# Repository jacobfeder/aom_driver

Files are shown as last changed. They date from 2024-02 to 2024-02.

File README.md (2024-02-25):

# 2-Tone AOM driver
This custom acousto-optic modulator (AOM) driver PCB is designed for generating short light pulses with enhanced isolation and power stability compared to traditional AOM configurations.

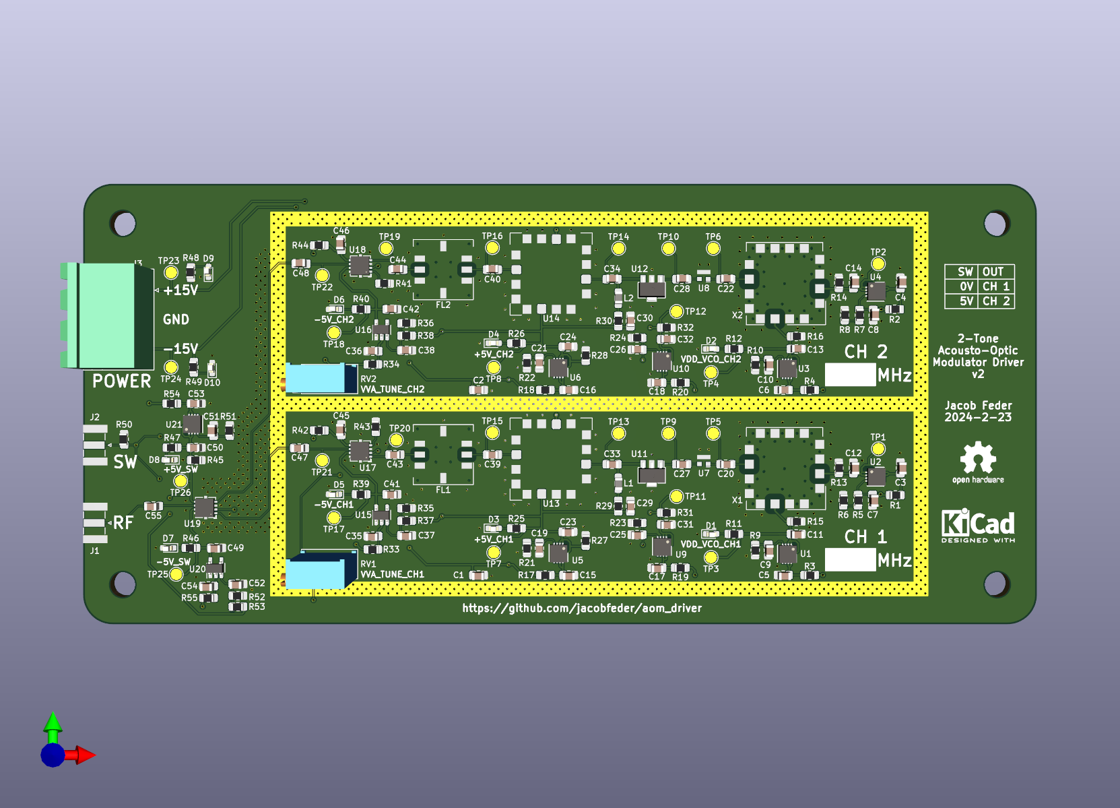
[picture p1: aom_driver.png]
AOM PCB rendering


# Background
When generating light pulses with an AOM, two parameters that you may care about are the isolation and power stability.

The isolation (usually expressed in dB) is defined as $10*\log_{10}(P_{on} / P_{off})$, where $P_{on}$ is the transmitted optical power with the AOM enabled, and $P_{off}$ is the transmitted optical power with the AOM disabled. A low isolation means that even when the AOM is disabled, there is significant light leakage through the AOM, which can be undesirable for certain applications.

Power stability is the change in transmitted optical power as a function of time or AOM duty cycle. The active area of an AOM that the optical beam passes through is made of a material whose optical index of refraction changes with strain (acoustic waves), producing the desired beam diffraction. However, other variables, such as temperature, can impact the index of refraction and, therefore, the pointing stability of the beam.

Many traditional AOM drivers are used as follows:
- The driver produces a single frequency which is toggled on and off, often with relatively low isolation.
- The optical power is switched between being primarily concentrated in the 0th order diffraction peak (AOM disabled, RF off) and the 1st order peak (AOM enabled, RF on).

This configuration produces two undesirable effects. First, drivers with low isolation (RF power $P_{on}/P_{off}$) can limit the optical isolation of the AOM due to parasitic driving of the AOM with RF leakage. Second, when switching the RF drive on/off, there is a change in RF power dissipation in the AOM crystal, inducing a temperature change. This temperature change reduces the beam pointing stability and produces power fluctuations as a function of time and switching duty cycle.

# Overview

The 2-Tone AOM driver greatly mitigates isolation and power stability issues. Whereas traditional AOM drivers rapidly switch between an RF signal being on or off, this driver rapidly switches between two different RF frequencies. The optical power diffracted by the AOM with low-frequency drive should ideally be fiber coupled into a single-mode fiber and then used in your down-stream application. The optical power diffracted by the AOM with the high-frequency "dummy" drive should be sent into a beam-dump. If the power of the two frequencies produced by this driver are properly calibrated, thermalization effects of the AOM crystal can be minimized because the RF power delivered to the crystal is equal for both frequencies. The driver can switch between these two frequencies with very high RF isolation such that the achievable AOM optical isolation will likely become limited by the physics of gaussian optics (see additional notes below).

# Specifications
- RF isolation ~90dB
- Both frequency outputs individually tunable from ~0dBm to <-30dBm (before amplifier, >30dBm after amplifier)
- Frequency range accessible with default VCO 140 - 250 MHz (much larger range possible by swapping VCO, see customization section)
- At the time of writing, cost is <$1000 for all parts
- Convenient DIN rail mounting
- TTL input switches between the two frequencies

# Principle of Operation
The driver consists of four main parts: two nearly-identical frequency synthesis sections, a fast RF switch to select the frequency, and an (off board) RF amplifier. The frequency synthesis sections begin with a voltage-controlled oscillator (VCO) that generates the initial RF signal (CVCO55xx). A fixed attenuator limits the maximum output power (PAT1220-C-x). Next, an amplifier increases the output power (GVA-81). A voltage-variable attenuator (VVA) allows the user to tune the output power of each frequency synthesis channel in real-time using a potentiometer in order to calibrate the system (RVA-3000R). A filter reduces some of the harmonics (RLP-xxx+). An RF switch (M3SWA-2-50DRB+) for each frequency synthesis channel toggles the frequency on/off before the final switch in order to increase isolation. This concludes the frequency synthesis sections. A final RF switch (M3SWA-2-50DRB+) selects the output frequency channel. The AOM driver output is intended to then be fed to an external RF amplifier.

# Required Parts
- The 2-tone AOM driver PCB (see aom_driver.csv for PCB BOM)
- +-15V DC power supply for the AOM driver PCB, recommend TODO
- RF amplifier, recommend [Minicircuits ZHL-03-5WF+](https://www.minicircuits.com/WebStore/dashboard.html?model=ZHL-03-5WF%2B)
- 24V DC power supply for the RF amplifier, recommend TODO

# Calibration
The goal of calibration is to adjust the output power of the two driver frequency channels such that they deliver the same RF power to the AOM crystal, minimizing power fluctuations due to thermalization. A good starting point is to measure the $S_{11}$ of the AOM itself using a network analyzer, and pick your two RF frequencies to have a similar $S_{11}$. Keeping the frequencies as far apart as possible may be important to maximize optical isolation (see additional notes section). Once the frequencies are selected, set up the whole system to drive the AOM. First, the primary frequency that will be used in your downstream application should be adjusted using the potentiometer to get the desired output RF power for the desired AOM diffraction efficiency. Keep in mind that using higher power will generally tend to exacerbate thermalization issues. Next, disconnect the driver PCB from the RF power amp and measure the output power of the driver PCB. Adjust the second "dummy" frequency to have similar power to the primary frequency. At this point, the two frequencies should be delivering pretty similar heat loads to the AOM. Final tuning can be performed by observing the pulse characteristics using a photodiode (with sufficient bandwidth). Connect the photodiode to an oscilloscope and toggle the AOM with very long period (e.g. 1 minute). You should be able to observe a fast rise (ns-scale, due to the AOM acoustic wave propagation), followed by a very slow drift (seconds-scale, due to thermalization). Now, finely adjust the dummy frequency until the the slow drift is minimized.

# Customization
The driver is designed to be easily customized. The critical components were chosen such that they can be swapped out with pin-pin compatible components with different characteristics.

### Frequency
The VCO can be substituted for nearly any member of the [Crystek CVCO55 series](https://www.crystek.com/home/vco/cvco55.aspx), which should accomodate a widge range of AOM drive frequencies. By default, the schematic is configured to output 150 MHz and 250 MHz. The VCO specified in the schematic has a range of 140 - 250 MHz. Changing the frequency in this range can be accomplished by configuring resistors $R_{5}$, $R_{6}$ for channel 1 and $R_{7}$, $R_{8}$ for channel 2. The VCO output frequency as a function of tuning voltage is given by the tuning curve in the [datasheet](https://www.crystek.com/specification/vco/CVCO55CW-0140-0250.pdf). The VCO tuning voltage is $10 \text{uA} * (R_5 + R_6)$ for channel 1, and $10 \text{uA} * (R_7 + R_8)$ for channel 2. For example, let's imagine you wanted an output frequency of 200 MHz on channel 1. The CVCO55CW-0140-0250 tuning curve shows that you would need a tuning voltage of 6 V. Then you would set $R_5 + R_6 = 6 \text{V} / 10 \text{uA} = 600 \text{kOhm}$. Similarly, resistors $R_{9}$ and $R_{10}$ set the VCO power supply voltages and can be substituted as needed according to $V_{CC1} = 10 \text{uA} * R_{9}$ and $V_{CC2} = 10 \text{uA} * R_{10}$. When changing the drive frequency, filters FL1 and FL2 should potentially be changed in order to accomodate the new frequency. They should be chosen such that the primary frequency is minimally attenuated, but harmonics are maximally attenuated. However, attenuating harmonics may not have a significant impact on the performance for reasons explained in the additional notes section.

### Power
The final RF output power of the system is impossible to predict precisely due to the tolerance stackup of all the components, which is why the board contains a potentiometer for individually tuning the output power of each frequency synthesis channel as well as a power-limiting fixed attenuator. The driver PCB should be capable of outputting a maximum power of >0dBm. The [Minicircuits ZHL-03-5WF+](https://www.minicircuits.com/WebStore/dashboard.html?model=ZHL-03-5WF%2B) has a gain of >30dB, so the final output power that can be achieved before the AOM is in excess of 1W. AOMs (and power amplifiers) can be damaged by too much input power. For this reason, a fixed attenuator PAT1220-C-x is included (U7 and U8) to limit the driver PCB maximum output power. Before connecting the driver PCB to the RF amplifier or AOM, the driver PCB output power should be measured. It is recommended to pick a specific PAT1220-C-x fixed attenuator for U7 and U8 in order to limit the maximum output power for your given RF amplifier and AOM such that no damage to either component is possible when the VVA poteniometer is tuned to output the maximum power from the driver PCB.

# Additional Notes
- The AOM driver system will cause the AOM to produce several optical beams at its output due to both AOM physics and RF design. When the low-frequency RF path is selected, it will produce 0th, 1st, 2nd, ..., nth order beams. The 1st order beam is the desired optical output and should go to the downstream application. All other 0th, 2nd, etc. order beams should be blocked or otherwise not coupled into the optical output. When the high frequency is selected, it will also produce 0th, 1st, 2nd, ..., nth order beams. All of these beams are "dummy" beams and should be blocked or otherwise not coupled into the downstream application. It is important to use the 1st order low-frequency beam for your application, as it will have minimal interference from RF drive harmonics.
- While the AOM driver has very high RF isolation, achieving high optical isolation requires additional careful attention to detail with optical design. I would recommend fiber coupling the 1st order low-frequency beam after the AOM for best performance.
- If all beams except the low-frequency 1st order beam are sufficiently blocked, the optical isolation will likely become limited by gaussian optics considerations. A beam of light entering the AOM will always have some finite divergence. After exiting the AOM, many beams are generated as explained above. These undesired beams will always have some degree of coupling into the desired output path due to their finite divergence, limiting the total optical isolation. A script is provided (TODO) to help with calculating the optical isolation. There is a somewhat intuitive explanation for this optics-limited isolation by consdering the tradeoff between isolation, rise-time, and AOM RF bandwidth. Getting a faster rise-time requires a smaller optical spot size on the AOM crystal, which requires a higher beam divergence. Higher divergence results in reduced isolation as explained above. Higher AOM RF bandwidth allows the primary and "dummy" beams to be separated by a larger angle, which increases their isolation. Therefore, it is important to consider the RF bandwidth when selecting an AOM, and the desired isolation and rise-time when selecting lenses to focus the beam onto the AOM crystal.

Feel free to email me if you have any questions at <jacobsfeder@gmail.com>.

# Acknowledgements
- This project would not have been possible without the help of Arron Campi at Gooch and Housego. He graciously provided his time and insight by helping me to understand AOM physics and limitations, as well as suggesting the idea of driving the AOM with multiple frequencies.
- Ben Soloway contributed the script that calculates optical isolation, and provided comic relief in addition to being my scientific partner in crime.
- The Awschalom Lab at UChicago and the NSF provided financial support.

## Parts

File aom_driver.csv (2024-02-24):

Source: | /home/jf/projects/aom_driver/aom_driver.kicad_sch
Date: | Sat 24 Feb 2024 12:10:03 PM CST
Tool: | Eeschema 7.0.10-7.0.10~ubuntu22.04.1
Generator: | /usr/share/kicad/plugins/bom_csv_grouped_by_value.py
Component Count: | 158
Collated Components:
Item | Qty | Reference(s) | Value | LibPart | Footprint | Datasheet | DNP | DKPN | MF | MFPN | Sim.Enable
1 | 43 | C1, C2, C3, C4, C5, C6, C11, C12, C13, C14, C15, C16, C17, C18, C20, C22, C23, C24, C27, C28, C29, C30, C31, C32, C33, C34, C35, C36, C39, C40, C41, C42, C43, C44, C45, C46, C47, C48, C49, C50, C53, C54, C55 | 2.2u | Device:C | Capacitor_SMD:C_0805_2012Metric_Pad1.18x1.45mm_HandSolder | ~ |  | 1276-2953-1-ND | Samsung Electro-Mechanics | CL21B225KAFNFNE
2 | 9 | C7, C8, C9, C10, C19, C21, C25, C26, C51 | 0.1u | Device:C | Capacitor_SMD:C_0805_2012Metric_Pad1.18x1.45mm_HandSolder | ~ |  | 1276-1099-1-ND | Samsung Electro-Mechanics | CL21B104KACNNNC
3 | 3 | C37, C38, C52 | 0.1u | Device:C | Capacitor_SMD:C_0805_2012Metric_Pad1.18x1.45mm_HandSolder | ~ | DNP | 1276-1099-1-ND | Samsung Electro-Mechanics | CL21B104KACNNNC
4 | 10 | D1, D2, D3, D4, D5, D6, D7, D8, D9, D10 | LED | Device:LED | LED_SMD:LED_0603_1608Metric_Pad1.05x0.95mm_HandSolder | ~ |  | 475-LTQ39G-Q1OO-25-1CT-ND | ams-OSRAM USA INC. | LT Q39G-Q1OO-25-1
5 | 1 | DRA1 | DIN_Rail_Adapter | Mechanical:DIN_Rail_Adapter |  | ~ |  |  | Winford Engineering | DINM30
6 | 1 | FL1 | RLP-320+ | RF_Filter:RLP-158 | RF_Mini-Circuits:Mini-Circuits_GP731_LandPatternPL-176 | https://www.minicircuits.com/pdfs/RLP-320+.pdf |  | 3157-RLP-320+CT-ND | Mini-Circuits | RLP-320+
7 | 1 | FL2 | RLP-158 | RF_Filter:RLP-158 | RF_Mini-Circuits:Mini-Circuits_GP731_LandPatternPL-176 | https://www.minicircuits.com/pdfs/RLP-158+.pdf |  | 3157-RLP-158+CT-ND | Mini-Circuits | RLP-158+
8 | 4 | H1, H2, H3, H4 | MountingHole | Mechanical:MountingHole | MountingHole:MountingHole_4.3mm_M4_DIN965 | ~ |  |  | McMaster-Carr | 91292A108
9 | 2 | J1, J2 | Conn_Coaxial | Connector:Conn_Coaxial | Connector_Coaxial:SMA_Samtec_SMA-J-P-X-ST-EM1_EdgeMount | ~ |  | 2057-RF2-143-T-17-50-G-ND | Adam Tech | RF2-143-T-17-50-G
10 | 1 | J3 | Screw_Terminal_01x03 | Connector:Screw_Terminal_01x03 | Connector_Phoenix_MSTB:PhoenixContact_MSTBA_2,5_3-G-5,08_1x03_P5.08mm_Horizontal | ~ |  | 277-1107-ND | Phoenix Contact | 1757255
11 | 1 | J4 | Screw_Terminal_01x03 | Connector:Screw_Terminal_01x03 |  | ~ |  | 277-1012-ND | Phoenix Contact | 1757022
12 | 2 | L1, L2 | 10u | Device:L | Inductor_SMD:L_0805_2012Metric_Pad1.05x1.20mm_HandSolder | ~ |  | 445-8656-1-ND | TDK Corporation | MLZ2012M100HT000
13 | 17 | R1, R2, R3, R4, R8, R17, R18, R19, R20, R29, R30, R33, R34, R42, R44, R54, R55 | 0 | Device:R | Resistor_SMD:R_0805_2012Metric_Pad1.20x1.40mm_HandSolder | ~ |  | 311-0.0ARCT-ND | YAGEO | RC0805JR-070RL
14 | 1 | R5 | 10M | Device:R | Resistor_SMD:R_0805_2012Metric_Pad1.20x1.40mm_HandSolder | ~ |  | 311-10.0MCRCT-ND | YAGEO | RC0805FR-0710ML
15 | 1 | R6 | 49.9k | Device:R | Resistor_SMD:R_0805_2012Metric_Pad1.20x1.40mm_HandSolder | ~ |  | 311-49.9KCRCT-ND | YAGEO | RC0805FR-0749K9L
16 | 1 | R7 | 150k | Device:R | Resistor_SMD:R_0805_2012Metric_Pad1.20x1.40mm_HandSolder | ~ |  | 311-150KCRCT-ND | YAGEO | RC0805FR-07150KL
17 | 11 | R9, R10, R21, R22, R35, R36, R37, R38, R51, R52, R53 | 499k | Device:R | Resistor_SMD:R_0805_2012Metric_Pad1.20x1.40mm_HandSolder | ~ |  | 311-499KCRCT-ND | YAGEO | RC0805FR-07499KL
18 | 8 | R11, R12, R25, R26, R39, R40, R46, R47 | 4.7k | Device:R | Resistor_SMD:R_0805_2012Metric_Pad1.20x1.40mm_HandSolder | ~ |  | 13-RC0805FR-134K7LCT-ND | YAGEO | RC0805FR-134K7L
19 | 9 | R13, R14, R15, R16, R27, R28, R31, R32, R45 | 1.5k | Device:R | Resistor_SMD:R_0805_2012Metric_Pad1.20x1.40mm_HandSolder | ~ |  | 311-1.50KCRCT-ND | YAGEO | RC0805FR-071K5L
20 | 2 | R23, R24 | 2.7M | Device:R | Resistor_SMD:R_0805_2012Metric_Pad1.20x1.40mm_HandSolder | ~ |  | 13-RC0805FR-072M7LCT-ND | YAGEO | RC0805FR-072M7L
21 | 3 | R41, R43, R50 | 49.9 | Device:R | Resistor_SMD:R_0805_2012Metric_Pad1.20x1.40mm_HandSolder | ~ |  | 311-49.9CRCT-ND | YAGEO | RC0805FR-0749R9L
22 | 2 | R48, R49 | 27k | Device:R | Resistor_SMD:R_0805_2012Metric_Pad1.20x1.40mm_HandSolder | ~ |  | 311-27.0KCRCT-ND | YAGEO | RC0805FR-0727KL
23 | 2 | RV1, RV2 | 2M | Device:R_Potentiometer | Potentiometer_THT:Potentiometer_Bourns_3296X_Horizontal | ~ |  | 3296X-205LF-ND | Bourns Inc. | 3296X-1-205LF
24 | 9 | U1, U2, U3, U4, U5, U6, U9, U10, U21 | LT3082xDD | Regulator_Linear:LT3082xDD | Package_DFN_QFN:DFN-8-1EP_3x3mm_P0.5mm_EP1.66x2.38mm | https://www.analog.com/media/en/technical-documentation/data-sheets/3082f.pdf |  | LT3082EDD#TRPBFCT-ND | Analog Devices Inc. | LT3082EDD#TRPBF
25 | 2 | U7, U8 | PAT1220-C-8DB | RF:PAT1220-C-8DB | RF_Converter:RF_Attenuator_Susumu_PAT1220 | https://www.susumu.co.jp/common/pdf/n_catalog_partition16_en.pdf |  | PAT120CT-ND | Susumu | PAT1220-C-0DB-T5
26 | 2 | U11, U12 | GVA-81 | RF_Amplifier:GVA-81 | Package_TO_SOT_SMD:SOT-89-3 | https://www.minicircuits.com/pdfs/GVA-81+.pdf |  | 3157-GVA-81+CT-ND | Mini-Circuits | GVA-81+
27 | 2 | U13, U14 | RVA-3000R | RF:RVA-3000R | RF_Mini-Circuits:Mini-Circuits_DV874_LandPatternPL-040 | https://www.minicircuits.com/pdfs/RVA-3000R+.pdf |  | 3157-RVA-3000R+CT-ND | Mini-Circuits | RVA-3000R+
28 | 3 | U15, U16, U20 | ADP7182AUJZ-5.0 | Regulator_Linear:ADP7182AUJZ-5.0 | Package_TO_SOT_SMD:TSOT-23-5 | https://www.analog.com/media/en/technical-documentation/data-sheets/ADP7182.pdf |  | 505-ADP7182AUJZ-5.0-R7CT-ND | Analog Devices Inc. | ADP7182AUJZ-5.0-R7
29 | 3 | U17, U18, U19 | M3SWA-2-50 | RF_Switch:M3SWA-2-50 | Package_DFN_QFN:Mini-Circuits_DL805 | https://www.minicircuits.com/pdfs/M3SWA-2-50DRB+.pdf |  | 3157-M3SWA-2-50DRB+CT-ND | Mini-Circuits | M3SWA-2-50DRB+
30 | 2 | X1, X2 | CVCO55xx | Oscillator:CVCO55xx | RF_Mini-Circuits:Mini-Circuits_CK605_LandPatternPL-012 | https://www.crystek.com/home/vco/cvco55.aspx |  | 744-1204-ND | Crystek Corporation | CVCO55CW-0140-0250

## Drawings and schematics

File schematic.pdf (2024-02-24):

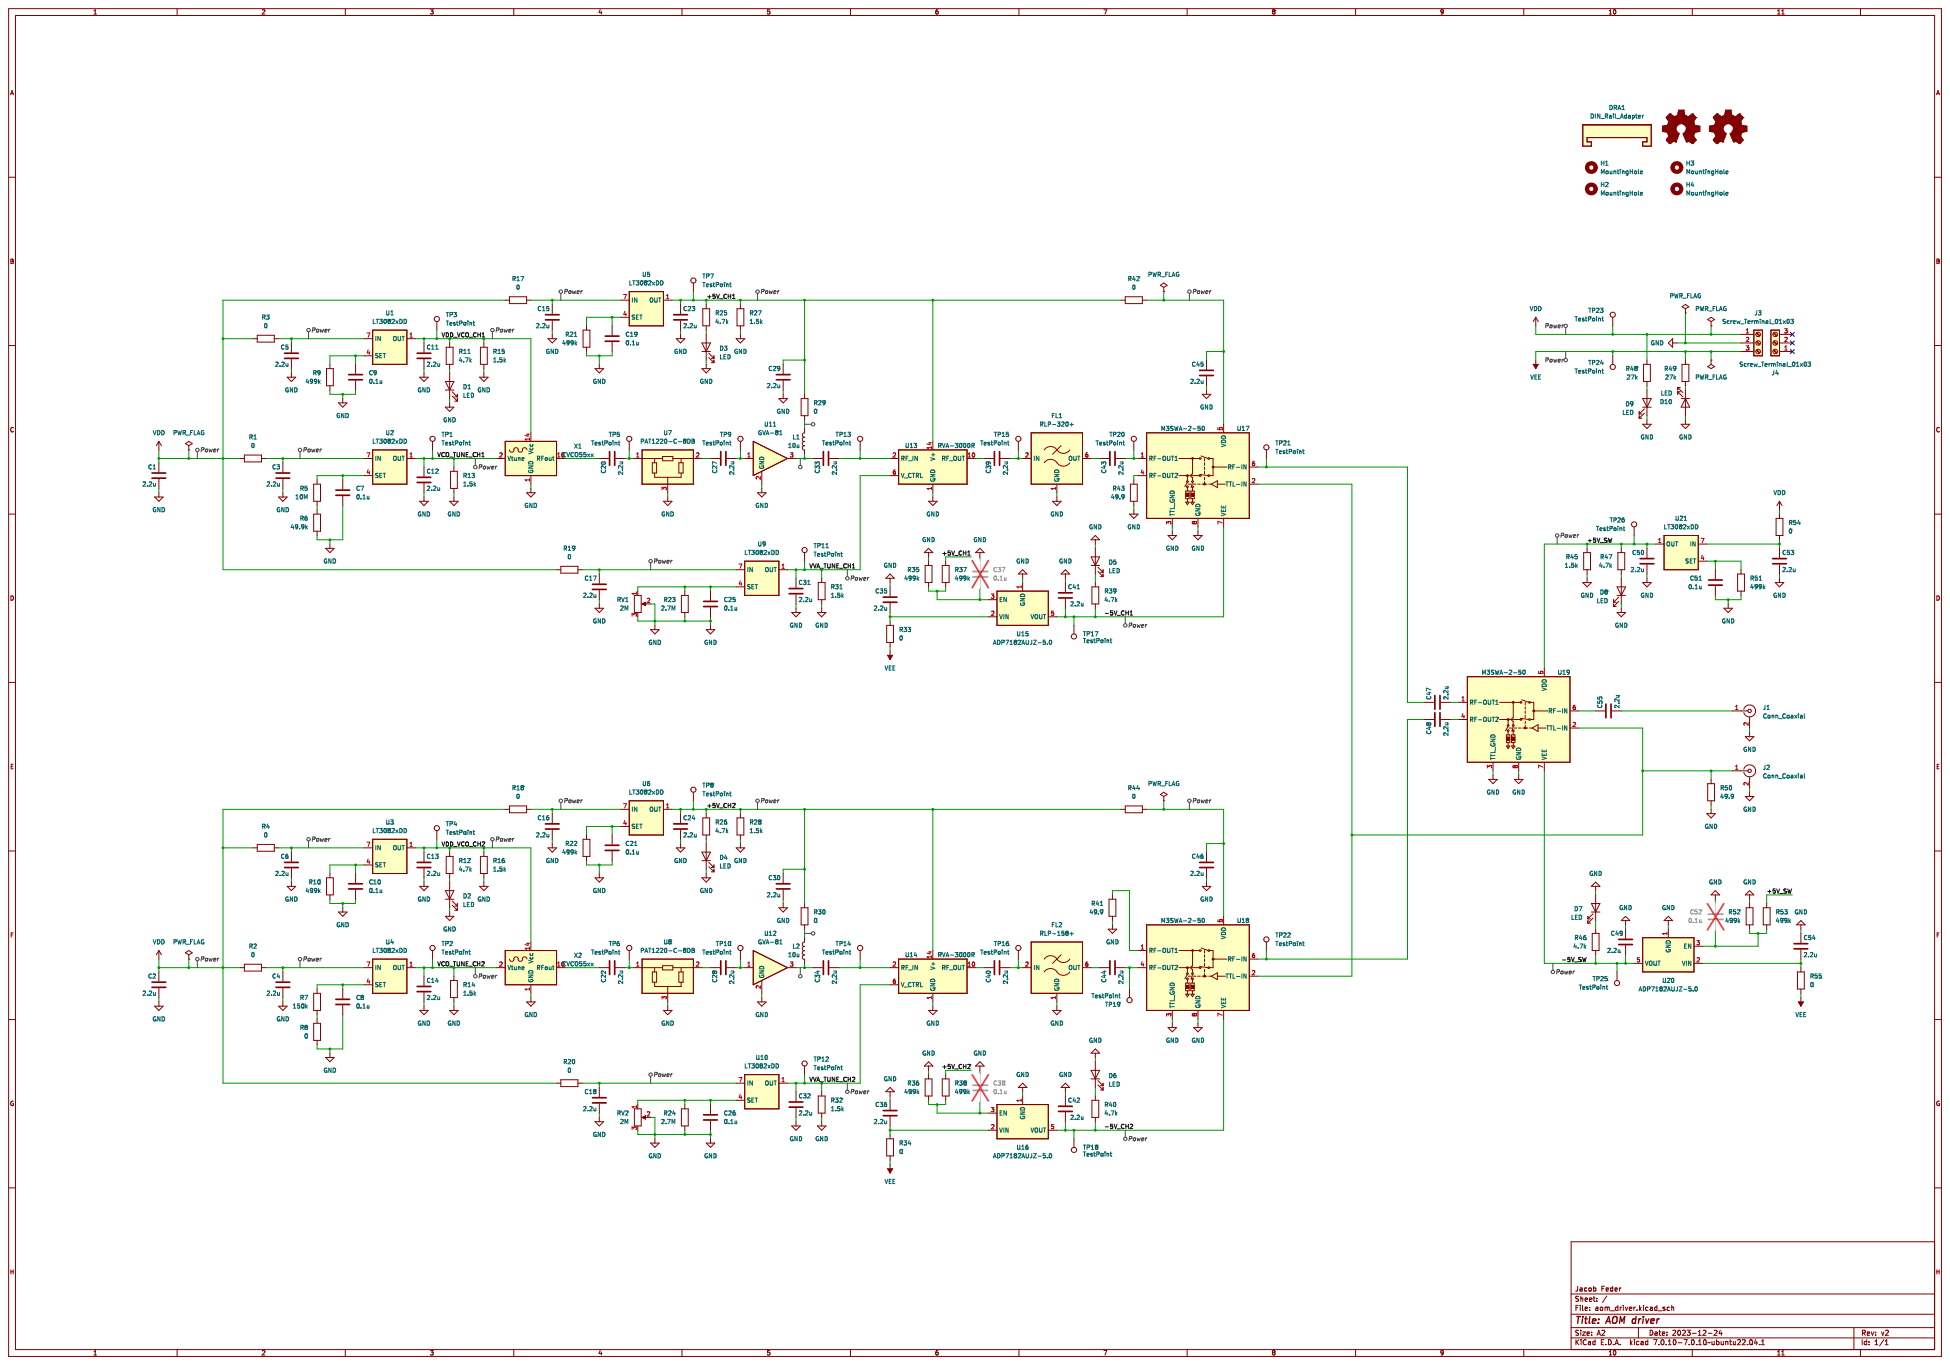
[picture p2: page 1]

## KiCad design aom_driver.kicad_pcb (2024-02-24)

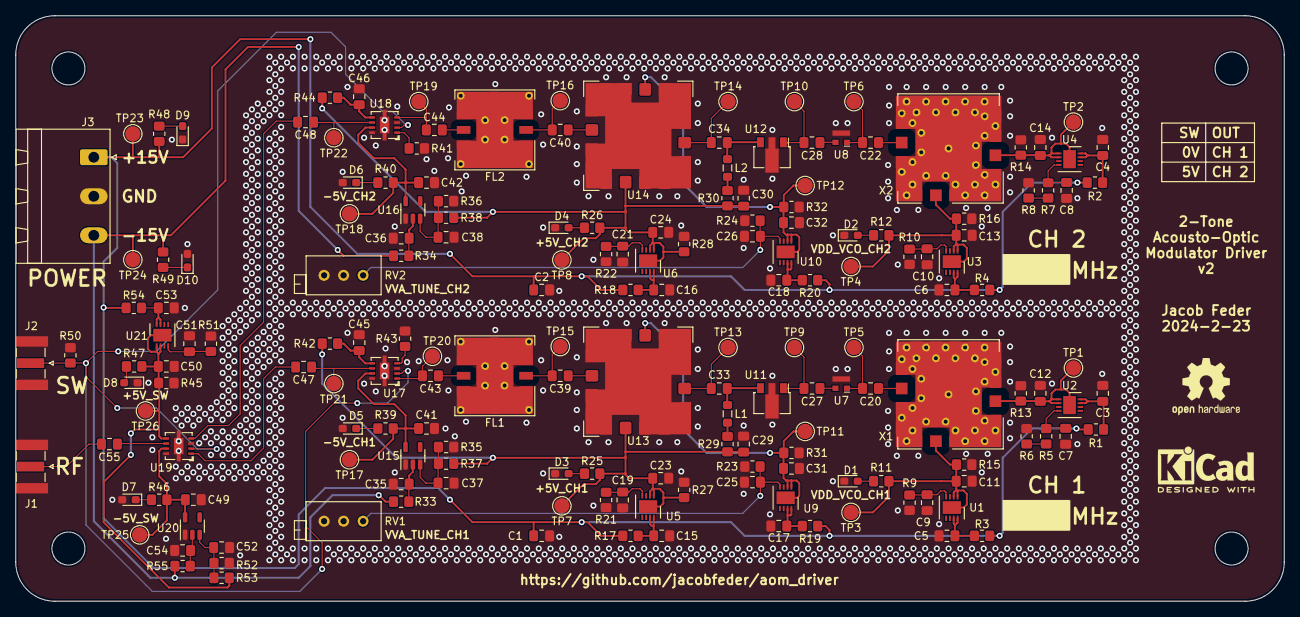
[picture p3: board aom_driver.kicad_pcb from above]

Board: 4 copper layers, 165.1 x 76.2 mm, 184 parts (0 on the bottom side), 84 nets.

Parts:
C1, C2, C3, C4, C5, C6, C11, C12, C13, C14, C15, C16, C17, C18, C20, C22, C23, C24, C27, C28, C29, C30, C31, C32, C33, C34, C35, C36, C39, C40, C41, C42, C43, C44, C45, C46, C47, C48, C49, C50, C53, C54, C55: 2.2u; C_0805_2012Metric_Pad1.18x1.45mm_HandSolder
C7, C8, C9, C10, C19, C21, C25, C26, C37, C38, C51, C52: 0.1u; C_0805_2012Metric_Pad1.18x1.45mm_HandSolder
D1, D2, D3, D4, D5, D6, D7, D8, D9, D10: LED; LED_0603_1608Metric_Pad1.05x0.95mm_HandSolder
FL1: RLP-320+; Mini-Circuits_GP731_LandPatternPL-176
FL2: RLP-158; Mini-Circuits_GP731_LandPatternPL-176
H1, H2, H3, H4: MountingHole; MountingHole_4.3mm_M4_DIN965
J1, J2: Conn_Coaxial; SMA_Samtec_SMA-J-P-X-ST-EM1_EdgeMount
J3: Screw_Terminal_01x03; PhoenixContact_MSTBA_2,5_3-G-5,08_1x03_P5.08mm_Horizontal
L1, L2: 10u; L_0805_2012Metric_Pad1.05x1.20mm_HandSolder
R1, R2, R3, R4, R8, R17, R18, R19, R20, R29, R30, R33, R34, R42, R44, R54, R55: 0; R_0805_2012Metric_Pad1.20x1.40mm_HandSolder
R5: 10M; R_0805_2012Metric_Pad1.20x1.40mm_HandSolder
R6: 49.9k; R_0805_2012Metric_Pad1.20x1.40mm_HandSolder
R7: 150k; R_0805_2012Metric_Pad1.20x1.40mm_HandSolder
R9, R10, R21, R22, R35, R36, R37, R38, R51, R52, R53: 499k; R_0805_2012Metric_Pad1.20x1.40mm_HandSolder
R11, R12, R25, R26, R39, R40, R46, R47: 4.7k; R_0805_2012Metric_Pad1.20x1.40mm_HandSolder
R13, R14, R15, R16, R27, R28, R31, R32, R45: 1.5k; R_0805_2012Metric_Pad1.20x1.40mm_HandSolder
R23, R24: 2.7M; R_0805_2012Metric_Pad1.20x1.40mm_HandSolder
R41, R43, R50: 49.9; R_0805_2012Metric_Pad1.20x1.40mm_HandSolder
R48, R49: 27k; R_0805_2012Metric_Pad1.20x1.40mm_HandSolder
RV1, RV2: 2M; Potentiometer_Bourns_3296X_Horizontal
SYM1: Logo_Open_Hardware_Small; OSHW-Logo2_9.8x8mm_SilkScreen
SYM2: Logo_Open_Hardware_Small; KiCad-Logo2_5mm_SilkScreen
TP1, TP2, TP3, TP4, TP5, TP6, TP7, TP8, TP9, TP10, TP11, TP12, TP13, TP14, TP15, TP16, TP17, TP18, TP19, TP20, TP21, TP22, TP23, TP24, TP25, TP26: TestPoint; TestPoint_Pad_D2.0mm
U1, U2, U3, U4, U5, U6, U9, U10, U21: LT3082xDD; DFN-8-1EP_3x3mm_P0.5mm_EP1.66x2.38mm
U7, U8: PAT1220-C-8DB; RF_Attenuator_Susumu_PAT1220
U11, U12: GVA-81; SOT-89-3
U13, U14: RVA-3000R; Mini-Circuits_DV874_LandPatternPL-040
U15, U16, U20: ADP7182AUJZ-5.0; TSOT-23-5
U17, U18, U19: M3SWA-2-50; Mini-Circuits_DL805
X1, X2: CVCO55xx; Mini-Circuits_CK605_LandPatternPL-012

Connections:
/+5V_CH1: C23.1, C29.1, R25.1, R27.1, R29.1, R37.1, R42.1, TP7.1, U5.1 (OUT), U5.2 (OUT), U5.9 (OUT), U13.14 (V+)
/+5V_CH2: C24.1, C30.1, R26.1, R28.1, R30.1, R38.1, R44.1, TP8.1, U6.1 (OUT), U6.2 (OUT), U6.9 (OUT), U14.14 (V+)
/+5V_SW: C50.1, R45.1, R47.1, R53.1, TP26.1, U19.5 (VDD), U21.1 (OUT), U21.2 (OUT), U21.9 (OUT)
/-5V_CH1: C41.2, R39.2, TP17.1, U15.5 (VOUT), U17.7 (VEE)
/-5V_CH2: C42.2, R40.2, TP18.1, U16.5 (VOUT), U18.7 (VEE)
/-5V_SW: C49.2, R46.2, TP25.1, U19.7 (VEE), U20.5 (VOUT)
/VCO_TUNE_CH1: C12.1, R13.1, TP1.1, U2.1 (OUT), U2.2 (OUT), U2.9 (OUT), X1.2 (Vtune)
/VCO_TUNE_CH2: C14.1, R14.1, TP2.1, U4.1 (OUT), U4.2 (OUT), U4.9 (OUT), X2.2 (Vtune)
/VDD_VCO_CH1: C11.1, R11.1, R15.1, TP3.1, U1.1 (OUT), U1.2 (OUT), U1.9 (OUT), X1.14 (Vcc)
/VDD_VCO_CH2: C13.1, R12.1, R16.1, TP4.1, U3.1 (OUT), U3.2 (OUT), U3.9 (OUT), X2.14 (Vcc)
/VVA_TUNE_CH1: C31.1, R31.1, TP11.1, U9.1 (OUT), U9.2 (OUT), U9.9 (OUT), U13.6 (V_CTRL)
/VVA_TUNE_CH2: C32.1, R32.1, TP12.1, U10.1 (OUT), U10.2 (OUT), U10.9 (OUT), U14.6 (V_CTRL)
GND: C1.2, C2.2, C3.2, C4.2, C5.2, C6.2, C7.2, C8.2, C9.2, C10.2, C11.2, C12.2, C13.2, C14.2, C15.2, C16.2, C17.2, C18.2, C19.2, C21.2, C23.2, C24.2, C25.2, C26.2, C29.2, C30.2, C31.2, C32.2, C35.1, C36.1, C37.1, C38.1, C41.1, C42.1, C45.2, C46.2, C49.1, C50.2, C51.2, C52.1, C53.2, C54.1, D1.1 (K), D2.1 (K), D3.1 (K), D4.1 (K), D5.2 (A), D6.2 (A), D7.2 (A), D8.1 (K), D9.1 (K), D10.2 (A), FL1.1 (GND), FL1.3 (GND), FL1.4 (GND), FL1.5 (GND), FL1.7 (GND), FL1.8 (GND), FL2.1 (GND), FL2.3 (GND), FL2.4 (GND), FL2.5 (GND), FL2.7 (GND), FL2.8 (GND), J1.2 (Ext), J2.2 (Ext), J3.2, R6.1, R8.2, R9.2, R10.2, R13.2, R14.2, R15.2, R16.2, R21.2, R22.2, R23.2, R24.2, R27.2, R28.2, R31.2, R32.2, R35.1, R36.1, R41.2, R43.2, R45.2, R50.2, R51.2, R52.1, RV1.2, RV1.3, RV2.2, RV2.3, U7.3, U8.3, U11.2 (GND), U12.2 (GND), U13.1 (GND), U13.3 (GND), U13.4 (GND), U13.5 (GND), U13.7 (GND), U13.8 (GND), U13.9 (GND), U13.11 (GND), U13.12 (GND), U13.13 (GND), U13.15 (GND), U13.16 (GND), U14.1 (GND), U14.3 (GND), U14.4 (GND), U14.5 (GND), U14.7 (GND), U14.8 (GND), U14.9 (GND), U14.11 (GND), U14.12 (GND), U14.13 (GND), U14.15 (GND), U14.16 (GND), U15.1 (GND), U16.1 (GND), U17.3 (TTL_GND), U17.8 (GND), U17.9 (GND), U18.3 (TTL_GND), U18.8 (GND), U18.9 (GND), U19.3 (TTL_GND), U19.8 (GND), U19.9 (GND), U20.1 (GND), X1.1 (GND), X1.3 (GND), X1.4 (GND), X1.5 (GND), X1.6 (GND), X1.7 (GND), X1.8 (GND), X1.9 (GND), X1.11 (GND), X1.12 (GND), X1.13 (GND), X1.15 (GND), X1.16 (GND), X2.1 (GND), X2.3 (GND), X2.4 (GND), X2.5 (GND), X2.6 (GND), X2.7 (GND), X2.8 (GND), X2.9 (GND), X2.11 (GND), X2.12 (GND), X2.13 (GND), X2.15 (GND), X2.16 (GND)
unnamed: C3.1, R1.2, U2.7 (IN), U2.8 (IN)
unnamed: C4.1, R2.2, U4.7 (IN), U4.8 (IN)
unnamed: C5.1, R3.2, U1.7 (IN), U1.8 (IN)
unnamed: C6.1, R4.2, U3.7 (IN), U3.8 (IN)
unnamed: C15.1, R17.2, U5.7 (IN), U5.8 (IN)
unnamed: C16.1, R18.2, U6.7 (IN), U6.8 (IN)
unnamed: C17.1, R19.2, U9.7 (IN), U9.8 (IN)
unnamed: C18.1, R20.2, U10.7 (IN), U10.8 (IN)
unnamed: C20.2, TP5.1, U7.1
unnamed: C22.2, TP6.1, U8.1
unnamed: C27.1, U7.2
unnamed: C27.2, TP9.1, U11.1
unnamed: C28.1, U8.2
unnamed: C28.2, TP10.1, U12.1
unnamed: C33.1, L1.2, U11.3
unnamed: C34.1, L2.2, U12.3
unnamed: C53.1, R54.2, U21.7 (IN), U21.8 (IN)
unnamed: D1.2 (A), R11.2
unnamed: D2.2 (A), R12.2
unnamed: D3.2 (A), R25.2
unnamed: D4.2 (A), R26.2
unnamed: D5.1 (K), R39.1
unnamed: D6.1 (K), R40.1
unnamed: D7.1 (K), R46.1
unnamed: D8.2 (A), R47.2
unnamed: D9.2 (A), R48.2
unnamed: D10.1 (K), R49.2
unnamed: C39.2, FL1.2 (IN), TP15.1
unnamed: C43.1, FL1.6 (OUT)
unnamed: C40.2, FL2.2 (IN), TP16.1
unnamed: C44.1, FL2.6 (OUT)
unnamed: C55.2, J1.1 (In)
unnamed: J2.1 (In), R50.1, U17.2 (TTL-IN), U18.2 (TTL-IN), U19.2 (TTL-IN)
unnamed: L1.1, R29.2
unnamed: L2.1, R30.2
unnamed: R5.2, R6.2
unnamed: R7.2, R8.1
unnamed: C9.1, R9.1, U1.4 (SET)
unnamed: C7.1, R5.1, U2.4 (SET)
unnamed: C10.1, R10.1, U3.4 (SET)
unnamed: C8.1, R7.1, U4.4 (SET)
unnamed: C19.1, R21.1, U5.4 (SET)
unnamed: C21.1, R22.1, U6.4 (SET)
unnamed: C25.1, R23.1, RV1.1, U9.4 (SET)
unnamed: C26.1, R24.1, RV2.1, U10.4 (SET)
unnamed: C33.2, TP13.1, U13.2 (RF_IN)
unnamed: C39.1, U13.10 (RF_OUT)
unnamed: C34.2, TP14.1, U14.2 (RF_IN)
unnamed: C40.1, U14.10 (RF_OUT)
unnamed: C37.2, R35.2, R37.2, U15.3 (EN)
unnamed: C35.2, R33.1, U15.2 (VIN)
unnamed: C38.2, R36.2, R38.2, U16.3 (EN)
unnamed: C36.2, R34.1, U16.2 (VIN)
unnamed: C47.1, TP21.1, U17.6 (RF-IN)
unnamed: C43.2, TP20.1, U17.1 (RF-OUT1)
unnamed: R43.1, U17.4 (RF-OUT2)
unnamed: C45.1, R42.2, U17.5 (VDD)
unnamed: C48.1, TP22.1, U18.6 (RF-IN)
unnamed: R41.1, U18.1 (RF-OUT1)
unnamed: C44.2, TP19.1, U18.4 (RF-OUT2)
unnamed: C46.1, R44.2, U18.5 (VDD)
unnamed: C55.1, U19.6 (RF-IN)
unnamed: C47.2, U19.1 (RF-OUT1)
unnamed: C48.2, U19.4 (RF-OUT2)
unnamed: C52.2, R52.2, R53.2, U20.3 (EN)
unnamed: C54.2, R55.1, U20.2 (VIN)
unnamed: C51.1, R51.1, U21.4 (SET)
unnamed: C20.1, X1.10 (RFout)
unnamed: C22.1, X2.10 (RFout)
VDD: C1.1, C2.1, J3.1, R1.1, R2.1, R3.1, R4.1, R17.1, R18.1, R19.1, R20.1, R48.1, R54.1, TP23.1
VEE: J3.3, R33.2, R34.2, R49.1, R55.2, TP24.1

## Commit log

2024-02-13 v1 design
    [aom_driver-B_Cu.gbr, aom_driver-B_Mask.gbr, aom_driver-B_Paste.gbr, aom_driver-B_Silkscreen.gbr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]
2024-02-24 Add details to README; add PCB BOM, schematic, PCB image
    [aom_driver.csv, aom_driver.kicad_sch]
2024-02-24 add PCB image to README
2024-02-25 add PCB schematic
2024-02-25 revert AOM PCB schematic in README
2024-02-25 regenerate gerbers to include paste file
    [aom_driver-B_Cu.gbr, aom_driver-B_Mask.gbr, aom_driver-B_Paste.gbr, aom_driver-B_Silkscreen.gbr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]
2024-02-25 add calibration section to README
